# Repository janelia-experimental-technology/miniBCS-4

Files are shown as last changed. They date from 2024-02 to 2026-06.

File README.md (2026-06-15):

# miniBSC-4
 Configurable I/O PCB for Teensy 4.1 and Max11300
 
 https://doi.org/10.25378/janelia.29669162

 System Overview

The miniBCS is a compact, general-purpose Behavioral Control System (BCS). It provides a powerful platform to control real-time experiments. It is highly adaptable in terms of types of outputs and connectors. It is also designed to be easy to use, self-documenting, inexpensive, and easy to customize.

Hardware Development

The miniBCS is designed around the Teensy processor system. Currently, the Teensy 3.5 processor board is being used. This board utilizes a 32-bit ARM processor with 120Mhz operation, 512K Flash, and 192K RAM. The Arduino programming environment makes writing and downloading code easy. A MAX11300 integrated circuit provides 12-bit bipolar ADC/DAC and other configurable IO not available on the Teensy. The various input/outputs (IOs) are brought out to various connector options, including DB9, BNC, latch connectors, and RJ9. Connectors can face vertically or horizontally. A waveform generator is also built in. builders can add a small monochrome graphic LCD and three pushbuttons to provide a simple user interface. The system is designed so that only the required features and connectors need to be added to the base board, minimizing cost and assembly time. The enclosure can be made from laser-cut material, making it easy to configure the unit, house the electronics, make attachment points, and engrave connector labels.

Capabilities (some are mutually exclusive):

    Up to three RS232 serial ports
    Host USB serial port (also used for programming)
    CAN bus
    Ethernet
    Up to 10 12-bit DACs with +/-5V, 0-10V, or -10 to 10V ranges (MAX11300)
    Up to 10 12-bit ADCs with 0-2.5, +/-5V, 0-10V, or -10 to 0V ranges (MAX11300)
    Up to 10 IOs with programmable thresholds or output ranges (MAX11300)
    8 isolated solenoid drivers with 11-35 Volt power supply range
    Frequency Generator with a range of 1Hz to 10MHz, sine, triangle, square wave
    2 temperature sensors (MAX11300)
    SPI/I2C Expansion Bus
    Up to 8 IOs that connect directly to the processor that can be programmed for:
        Interrupts
        0-3.3V DAC
        0-3.3V ADC
        3.3V digital output
        5V tolerant digital input
        PWM or servo drive
        Various timer/counter needs

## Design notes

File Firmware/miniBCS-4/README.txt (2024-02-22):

# mimiBCS

An Arduino library to provide a high level interface for the miniBCS
This version handles boards from REV M and up

The miniBCS is an interface board for the Teensy 4.1 that provides BNC connections, Ethernet connection, I/O Expansion via a Maxim chip, 
drivers for RS232, solenoid drivers, encoder interface, and a waveform generator.

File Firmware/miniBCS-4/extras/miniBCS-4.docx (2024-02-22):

SPI LCD Panel Configuration and Setup

20170106 sws ID&F

The SPI-LCD (Serial Peripheral Interface Liquid Crystal Display) is used in lieu of the serial LCD panel in order to free up an additional serial port when needed to communicate with other peripheral devices. It is physically a direct replacement for the serial display, however, the Serial.print commands cannot be used with this display.

Firmware

The SPI-LCD library must be installed and the header file must be included at the top of the program:

#include <LCD2X16.h>

You need to create an instance of the LCD object outside of any functions:

LCD2x16 lcd;

The name ‘lcd’ is arbitrary. The examples assume ‘lcd’ is used as the object’s name.

In ‘setup()’ initialize the driver:

lcd.begin();

This will locate which SPI connector the board is connected to.

The following functions are available:

uint8_t csPin = lcd.getID();

Returns the number of the chip select pin for the display. This will depend on which SPI port the display is plugged into. There is generally no need to use this function.

lcd.setBacklight(uint8_t level);

Set the backlight level. ‘level’ should be between 0 and 8.

lcd.cls();

Clear the display.

lcd.write(char * string);

Write the character string ‘string’ to the display at the current cursor location.

lcd.setPosition(uint8_t row, uint8_t col);

Set the cursor to row ‘row’ and column ‘col’ – the top row is 0 and the left-most column is 0.

lcd.wrbyte(char c);

Send a single byte to the LCD. This can be used to send other display commands, such as setting special characters. See the NHD‐0216K3Z‐FL‐GBW‐V3 data sheet for details.

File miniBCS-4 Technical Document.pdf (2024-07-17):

# miniBCS-4

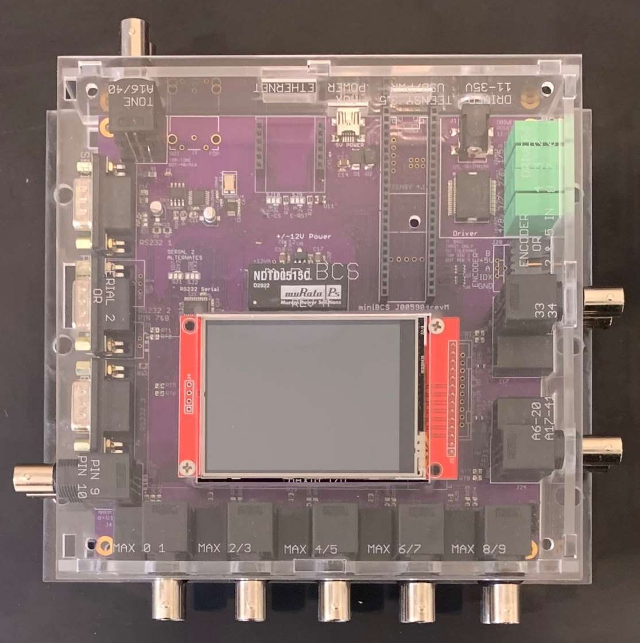
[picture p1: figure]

### Steve Sawtelle Engineer, ID&F

### Contents

System Overview | 2
Hardware Development | 2
Assembly | 4
Firmware | 6
miniBCS-4 Library Functions | 7
Enclosure | 8
Minimal Assembly of Bare PCB | 8

### System Overview

The miniBCS-4 is a compact, general purpose multi-function I/O system that makes it easy to access various peripherals found on the Teensy 4.1 and provides a powerful platform to control real time experiments. It is highly adaptable in terms of types of outputs and connectors and is designed to be easy to use, inexpensive, and easy to customize.

### Hardware Development

The miniBCS-4 is designed around the Teensy processor system. Currently, the Teensy 4.1 processor board is being used. The Arduino programming environment makes writing and downloading code easy. A MAX11300 integrated circuit is used to provide 12-bit bipolar ADC/DAC and other configurable I/O not available on the Teensy. The various input/outputs (IOs) are brought out to various connector options including DB9, BNC, latch connectors, and RJ9. A waveform generator is also built in. A color graphic LCD with touchscreen can be added to provide a simple user interface. Various sensors and other extensions can be easily added using I2C communications via a Qwiic connector and an SPI connector. The system is designed so that only the required features and connectors needed for a particular application are added to the base board, minimizing cost and assembly time. The enclosure can be made from laser cut acrylic, which makes it easy to configure the unit, house the electronics, make attachment points, and engrave connector labels.

Capabilities (some are mutually exclusive):

- Up to three RS232 serial ports
- Host USB serial port (also used for programming)
- Ethernet via WIZnet module
- Incremental Encoder (optional index pin) with 5V tolerant inputs
- Up to 10 12-bit DACs with +/-5V, 0-10V, or -10 to 10V ranges (MAX11300)
- Up to 10 12-bit ADCs with 0-2.5, +/-5V, 0-10V, or -10 to 0V ranges (MAX11300)
- Up to 10 I/Os with programmable thresholds or output ranges (MAX11300)
- 8 isolated solenoid drivers with 11-35 Volt power supply range
- Frequency Generator with range of 1Hz to 10MHz, sine, triangle, or square wave
- I/O Extension providing two direct processor I/Os and ten Maxim I/Os
- QWIIC I2C (as I2C number 2)
- SPI witn two chip selects
- Up to 9 I/Os that connect directly to the processor that can be programmed for: o Interrupts
o 0-3.3V ADC
o 3.3V digital output
o 3.3 digital input
o PWM or servo drive
o Various timer/counter needs

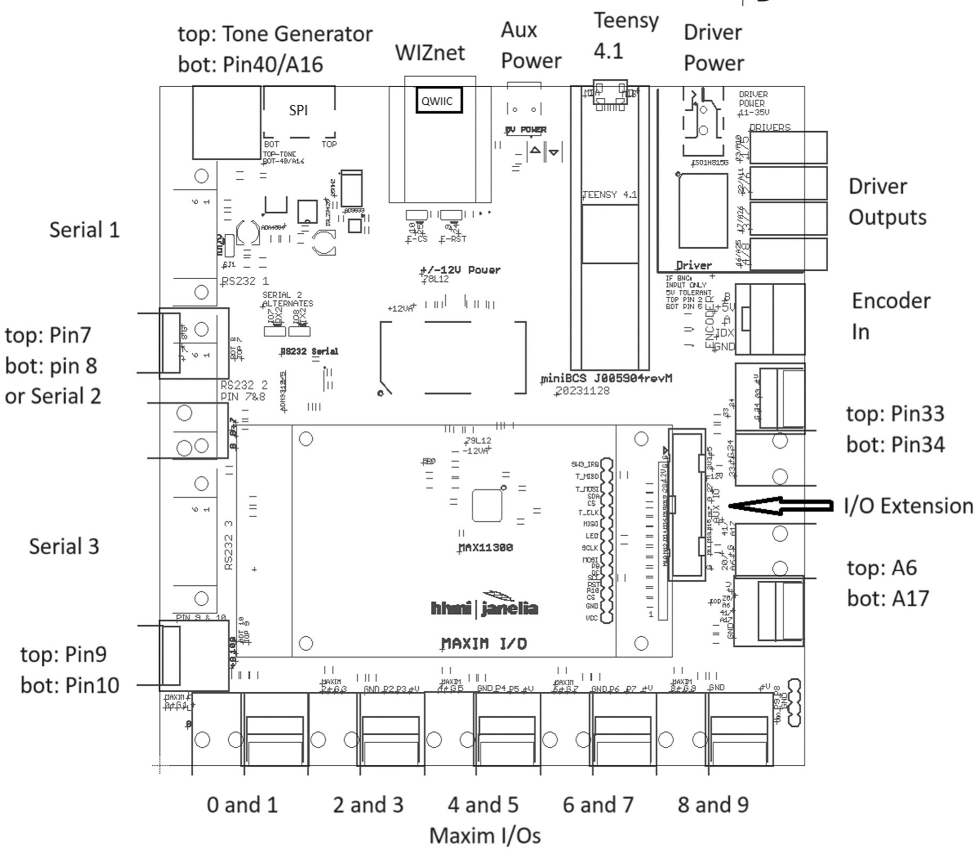
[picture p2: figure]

### Assembly

Due to the relative low cost and relative assembly difficulty of the surface mount parts on the board, it is advisable to have the basic board assembled by a small run assembly house. For 10 boards, this can be done for about $300 a board. For hand assembling partial boards, there is information at the end of the document. The real customization of the board is done by hardware jumpers, choice of connectors, and firmware. The jumpers and connectors can be easily soldered by hand by novices.

Note on Jumpers

Jumpers are included on the board to allow various configurations. There are two types of jumpers; I/O select, and tone select.

Pin selection jumpers have a connection to the default I/O. If the alternate function is needed, then the default connection between the pads needs to be cut and a short between the other function and the middle pad needs to be soldered in. These are used to select alternate CPU pins to be available at each connector to maximize I/O options. The following selections are available:

I/O | Jumper Name | Default | Option (cut and jumper)
RX2/IO7 | SJ1 | RS232 #2 Receive | Pin 7 (PWM, digital I/O)
TX2/IO8 | SJ2 | RS232 #2 Transmit | Pin 8 (PWM, digital I/O)
Eth-RST/IO9 | SJ9 | Pin 9 (PWM, digital I/O) | Alternate Ethernet Reset on Pin 9
Eth-CS/IO10 | SJ10 | Pin 10 (PWM, digital I/O) | Alternate Ethernet CS Pin 10

Tone Generator jumper (SJ1) allows the tone generator to bypass AC coupling and gain to provide a TTL square wave output. The default supports sine/triangle tones and AC couples the signal and provides variable gain. If a TTL square wave output is needed, then cut the jumper and solder the pads for square wave output. This bypasses the AC coupling and variable gain.

I2C (J11) provides a QWIIC compatible I2C interface using SDA2 and SCL2 from the Teesny 4.1. Be sure to specify ‘Wire2’ when setting the I2C clock and other initialization.

SPI (J3 or J26) provides an SPIO interface using either a ten-pin ribbon cable or a 7-pin 0.1 center connector. The ribbon cable is preferred as it provides grounds between the signals. Teensy pins 9 and 10 are brought out as chip selects, which would preclude their use on the J18/J19 connectors next to Serial Port 3.

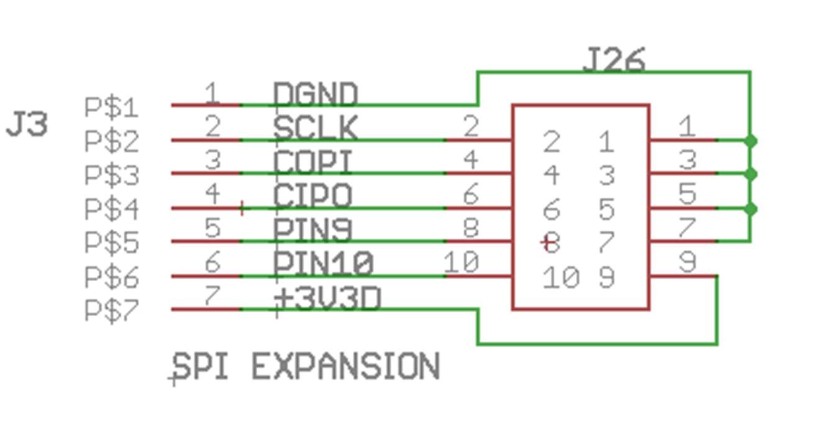
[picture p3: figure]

Auxiliary Input/Output (X2) Provides additional I/O through a 20-pin ribbon cable. Two unused Teensy I/O pins are brought out, along with the upper ten Maxim I/O pins, and power.

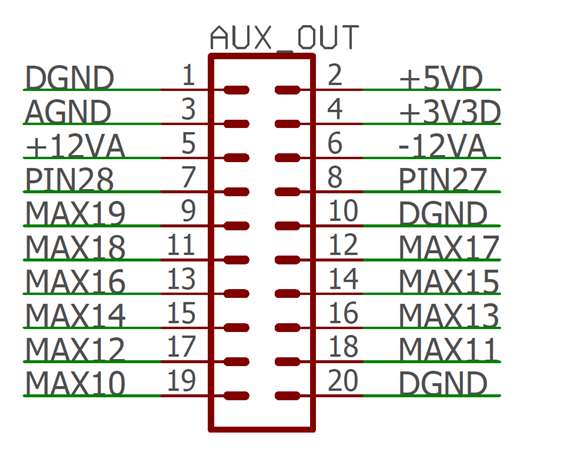
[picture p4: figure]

The available pins are:

### 1. Digital ground

2. +5 volts

### 3. Analog ground

4. +3.3 volts
5. +12 volts
6. -12 volts

### 7. Teensy pin 28 8. Teensy pin 27 9. Maxim I/O pin 19 10. Digital ground 11. Maxim I/O pin 18 12. Maxim I/O pin 17 13. Maxim I/O pin 16 14. Maxim I/O pin 15 15. Maxim I/O pin 14 16. Maxim I/O pin 13 17. Maxim I/O pin 12 18. Maxim I/O pin 11 19. Maxim I/O pin 10 20. Digital ground

### Firmware

The firmware is written under the Arduino environment. Download and install the Arduino software and add in the Teensy support. See the Arduino and PJRC websites for current implementations.

Add the miniBCS-4 library to your Arduino environment. This is available on the jET Experimental Technologies GitHub repository. This provides high level access to the drivers, tone generator, and encoder.

If the MAX11300 is used, add the MAX11300 library, also on the jET Experimental Technologies GitHub repository.

If the LCD is used, you will need to add the following Adafruit LCD libraries:

XPT2046_Touchscreen for Touchscreen functions.
ILI9341_t3.h for TFT Display functions.

The Adafruit website has good tutorial on how to use their functions.

Finally, if it is desired to have a command interface, then it may be worthwhile to look at the CmdArduino library, also found on the jET Experimental Technologies GitHub repository.

### miniBCS-4 Library Functions

These functions are available through the miniBCS-4 Arduino library.

void begin();
sets up hardware for I/O and interrupts
void driverOn(uint8_t ch);
turn on solenoid driver channel ‘ch’ void driverOff(uint8_t ch);
turn off solenoid driver ‘ch’
uint32_t getVersion(void);
return firmware version (year, month, day concatenated into a single integer – ex: 20190230 void setToneGain(uint8_t level);
set gain of tone output (0-255)
void toneReset(void);
reset frequency generator chip
int8_t setTone( float freq, uint16_t mode);
set tone to frequency ‘freq’ (1 to 20 MHz), and mode: TONE_SINE sine wave
TONE_TRIANGLE triangle wave TONE_SQUARE square wave
void toneOn(void);
enable tone output
void toneOff(void);
disable tone output
int32_t getPosition(void);
get encoder counts
void setPosition(uint32_t newpos);

set current value for encoder counts.

### Enclosure

An enclosure can be made from 1/8” laser cut acrylic. This allows the enclosure to be easily customized for the particular set of I/O connections mounted on the PCB. It also allows engraving unique labels for each connector.

A DXF file is provided that shows all the possible cutouts for various connector combinations.

### Minimal Assembly of Bare PCB

Only the parts needed for the application need to be assembled to the printed circuit board (PCB). At a minimum, the Teensy must be installed; everything else is optional. However, it is probably better to buy boards with all surface mount parts mounted and then add any required connectors and jumpers.

To decide what parts to install, first list the IOs needed for the application, then determine which IOs on the miniBCS-4 can fill the requirement. If only a few basic 0-3.3V digital and analog IOs are needed, the MAX11300 IC can be eliminated along with the DC-DC converter, power USB connector, and regulators. The parts that need to be added when the MAX11300 functions are needed are outlined on the PCB. If no solenoids, relays, or other power actuators are needed, the parts outlined in the solenoid driver area can be eliminated. If RS232 serial is not needed, then do not install the parts outlined in the RS232 area and change the jumper defaults for SJ1 and SJ2 by cutting the TX2 and RX2 track to the center pad and soldering from IO7 and IO8 to the center pad. This allows these pins to be used for additional IO.

Each IO will require a connector and in-line resistor (typically 100 ohms) or thermal cutout (PTC – such as the Murata PRG18BB series.

Minimal assembly:
Solder the headers for the Teensy

If any other ICs will be mounted, then D1 and D2 need to be installed.

If the MAX11300 functions are needed,
Add in the DC-DC converter, regulators, and filter caps, and resistors in that area. Solder in the components within that area

The connectors for each port pair can be:

### 1 Molex 0855135016 right angle RJ9 1 Amphenol 112705 right angle dual BNC

Both can coexist on the circuit board, but only one or the other should be connected to external circuits.

If the encoder is needed,
Solder in a TE 103635-4 right angle header
Mount U2. If the index pin is needed, then also add U8.

If the LCD is required
Solder a header in at LCD1. This can be a pluggable header or a flex cable to allow the LCD to be positioned elsewhere. A flex cable such as A9AAT-090xF can be used, where ‘x’ is the length in inches, 2, 3, 4, 5, 6, or 8.

If the solenoid driver is required
Solder the components in the Solenoid Parts area.

If RS232 serial ports are required
Solder in the parts in the RS232 Parts area
Solder in, for each port:

### 1 Norcomp 190-009-163R001 right angle DB9

If serial port 2 is not need, the pins can be brought out as additional I/O by cutting the serial jumpers SJ1 and SJ2 and solder jumper the alternate configuration pads.

If the tone generator is required
Solder in the parts in the TONE area. Also, if a TTL square wave is required, instead of the sine/triangle output cut the jumper at SJ3 and solder the alternative configuration.

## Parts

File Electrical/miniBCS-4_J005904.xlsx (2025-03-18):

J005904_miniBCSrevM- Three Serial Ports
Qty | Value | Device | Designators | Manufacturer | Man PN | Vendor | Vendor PN | $ea | $Total | Notes
2 | cap | CAP ALUM 22UF 20% 6.3V SMD | C9 C13 | Nichicon | UZP0J220MCL1GB | DK | 493-10070-1-ND | $0.50 | $1.00
1 | dc-dc | CONV DC/DC 3W 5VIN 15VOUT DIP24 | PS1 | Traco Power | TEN 3-0523N | DK | TEN3-0523N-ND | $16.40 | $16.40
1 | power in | CONN PWR JACK 2.5X5.5MM SOLDER | J1 | CUI | PJ-002BH-SMT-TR | DK | CP-002BHPJCT-ND | $1.29 | $1.29
2 | Schottky Diode | DIODE SCHOTTKY 15V 1A DO214AC | D1 D2 | Microsemi Corporation | LSM115JE3/TR13 | DK | LSM115JE3/TR13CT-ND | $1.17 | $2.34
24 | 0.1 | CAP CER 0.1UF 50V X7R 0603 | C1 C4 C6 C7 C8 C10 C14 C15 C19 C20 C21 C23 C24 C25 C26 C28 C29 C33 C34 C37 C38 C39 C40 C41 | Kemet | C0603C104K5RACTU | DK | 399-5089-1-ND | $0.03 | $0.72
1 | 0.1 | CAPS0805S | C16 |  |  | DK
1 | 1 | CAP CER 1UF 50V X7R 0805 | C11 | Kemet | C0805C105K5RACTU | DK | 399-7409-1-ND | $0.22 | $0.22
2 | 2K70 | RES SMD 2.7K OHM 1% 1/8W 0805 | R8 R13 | Vishay Dale | CRCW08052K70FKTA | DK | 541-2.70KCCT-ND | $0.05 | $0.10
6 | 4K99 | RES SMD 4.99K OHM 1% 1/8W 0805 | R2 R3 R6 R7 R26 R27 | Vishay Dale | CRCW08054K99FKEA | DK | 541-4.99KCCT-ND | $0.05 | $0.30
2 | 4R99 | RESISTOR_SM0805S | R14 R28 | Vishay Dale | CRCW08054R99FNEA | DK | 541-4.99CCT-ND | $0.06 | $0.12
2 | 10K0 | RES SMD 10K OHM 1% 1/8W 0805 | R16 R20 | Vishay Dale | CRCW080510K0FKTA | DK | 541-3016-1-ND | $0.14 | $0.28
9 | 10uF | CAP CER 10UF 25V X7R 1206 | C12 C17 C18 C27 C30 C31 C32 C35 C36 | Kemet | C1206C106M3RACTU | DK | 399-7443-1-ND | $0.51 | $4.59
1 | 78L12F | IC REG LDO 12V 0.1A SOT89-3 | U6 | ST Micro | L78L12ACUTR | DK | 497-1195-1-ND | $0.37 | $0.37
1 | 79L12 | IC REG LDO -12V 0.1A SOT89-3 | U9 | STMicro | L79L12ACUTR | DK | 497-7301-1-ND | $0.38 | $0.38
38 | 100 | THERMISTOR PTC 100 OHM SMD | RP1 - RP23, RT1 -RT8 | Murata | PRG18BB101MB1RB | DK | 490-2469-1-ND | $0.45 | $17.10
8 | 100 | RESISTOR_SM0805S | R1 R5 R17 R21 R22 R23 R24 R25 |  |  | DK
3 | 118 | RES SMD 118 OHM 1% 1/8W 0805 | R12 R15 R19 | Vishay Dale | CRCW0805118RFKEA | DK | 541-118CCT-ND | $0.05 | $0.15
1 | 1K25 | RES SMD 1K OHM 1% 1/8W 0805 | R4 | Vishay Dale | CRCW08051K00FKTA | DK | 541-1.00KAWCT-ND | $0.13 | $0.13 | ???
1 | AD9833 | IC WAVEFORM GEN PROG 10MSOP | U4 | Analog Devices | AD9833BRMZ-REEL7 | DK | AD9833BRMZ-REEL7CT-ND | $9.34 | $9.34
1 | ADA4084 | IC OPAMP GP 15.9MHZ RRO 8SOIC | U1 | Analog Devices | ADA4084-2ARZ-R7 | DK | ADA4084-2ARZ-R7CT-ND | $6.70 | $6.70
1 | ADM3312/5 | C TXRX RS-232 3:3 2.7V 24TSSOP | U7 | Analog Devices | ADM3312EARUZ-REEL7 | DK | ADM3312EARUZ-REEL7CT-ND | $3.50 | $3.50
1 | ISL23425 | ISL2342IC DGTL POT DUAL 10K 14TSSOP 5 | U3 | Intersil | ISL23425WFVZ-T7A | DK | ISL23425WFVZ-T7ACT-ND | $2.47 | $2.47
1 | ISO1H815G | IC SWITCH HISIDE 8CH DSO-36 | U5 | Infinion | ISO1H815G | DK | ISO1H815GCT-ND | $10.75 | $10.75
1 | MAX11300GCM | IC ADC 12BIT 48-TQFP | U10 | Maxim | MAX11300GCM+ | DK | MAX11300GCM+-ND | $14.74 | $14.74
1 | OSC-OE-CFPS-9 | 25MHz CMOS XO | X1 | AVX | KC5032A25.0000CM0E00 | DK | 1253-1043-1-ND | $1.46 | $1.46
2 | TEENSY_3_5_2 | CONN RCPT .100" 24POS SNGL GOLD | M1A, M1B | Samtec | SSQ-124-02-G-S | DK | SAM1187-24-ND | $4.64 | $9.28
1 | UX60-MB-5ST | CONN RECEPT MINI USB2.0 5POS | J2 | TE | 1734035-2 | DK | A31727CT-ND | $0.87 | $0.87
1 | CAT811 | IC SUPERVISOR PP ACT LO SOT143-4 | U11 | ON Semiconductor | CAT811TTBI-GT3 | DK | CAT811TTBI-GT3OSCT-ND | $0.43 | $0.43
 |  |  |  |  |  |  |  |  | $0.00
4 | Terminal Block | TERM BLOCK HDR 4POS 90DEG 2.5MM | J5 J6 J7 J8 | Phoenix | 1894804 | DK | 1894804-ND | $2.67 | $10.68
8 | plug for 1894804 | TERM BLOCK PLUG 2POS STR 2.5MM |  | Phoenix | 1881325 | DK | 277-1430-ND | $3.10 | $24.80
3 | DB9 | CONN DSUB PLUG 9POS SMD R/A SLDR | P1 P2 P3 | NorComp Inc. | 190-009-163R001 | DK | 190-09MA-ND | $2.85 | $8.55
 |  |  |  |  |  |  |  |  | $0.00
9 | Signal Alternate - BNC | BNC-DUAL | J4 J14 J19 J22 J27 J28 J29 J30 J31 | Amphenol | 112705 | DK | ACX2286-ND | $7.62 | $68.58
7 | Signal Alternate - RJ9 | CONN MOD JACK 4P4C R/A UNSHLD | J17 J21 J42 J43 J44 J45 J46 | Molex | 432024101 | DK | WM5439-ND | $1.54 | $10.78
 |  |  |  |  |  |  |  |  | $0.00
1 | Encoder | CONN HEADER R/A 4POS 2.54MM | J10 | TE Connectivity AMP Connectors | 5-103635-4 |  | A33864-ND | $1.39 | $1.39
 |  |  |  |  |  |  |  |  | $0.00
1 | Display | Color 320x240 TFT Touchscreen, ILI9341 Controller Chip | LCD1 | PJRC | DISPLAY_ILI9341_TOUCH | DK |  | $15.00 | $15.00
4 | LCD support | HEX STANDOFF #4-40 NYLON 1" |  |  | 4848 | DK | 36-4848-ND | $1.05 | $4.20
1 | LCD cable | FLEX CABLE - AFF14G/AF14/AFE14T | LCD1 | TE Connectivity AMP Connectors | A9BAG-1402F |  | A9BAG-1402F-ND | $4.89 | $4.89
1 | SPI connector | CONN HEADER R/A 10POS 2.54MM | J26 | 3M | 30310-5002HB |  | 3M15452-ND | $1.01 | $1.01
1 | qwiic Connector | Surface Mount, Right Angle 4 pos 1.00mm | J11 | JST Sales America Inc. | SM04B-SRSS-TB |  | 455-SM04B-SRSS-TBCT-ND | $0.60 | $0.60
2 | 2ch buffers | IC BUF NON-INVERT 5.5V SOT23-6 | U2 U8 | TI | SN74LVC2G17DBVR |  | 296-SN74LVC2G17DBVRCT-ND | $0.40 | $0.80
1 | Networking Modules W5500 + MAG Jack |  |  | WIZnet | WIZ850IO |  |  | $21.98 | $21.98
2 | Headers & Wire Housings Tiger Buy Socket Strip with Square Tails, 0.100 Pitch |  |  | Samtec | SSQ-106-01-G-S |  |  | $1.35 | $2.70
 |  |  |  |  |  |  |  |  | $280.99

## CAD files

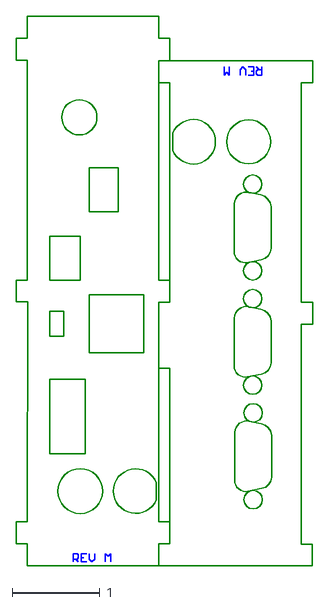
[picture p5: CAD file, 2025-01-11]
Mechanical/untitled.dxf
3.37 x 6.25

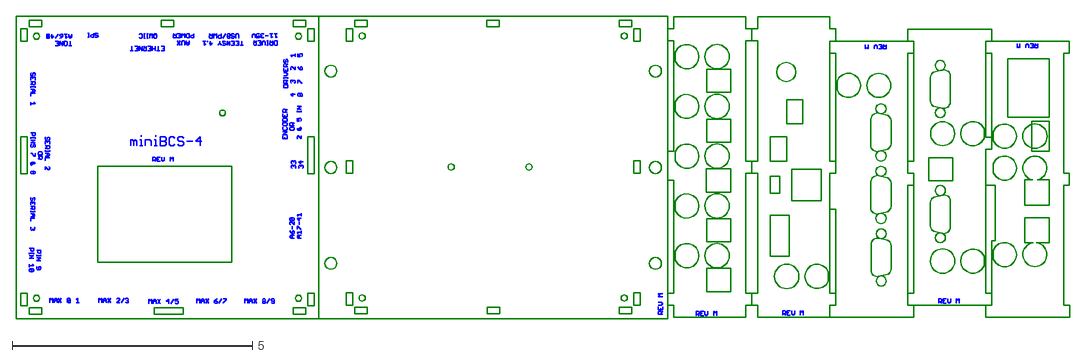
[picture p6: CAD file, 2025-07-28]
Mechanical/J005904_miniBCS-4.dxf
21.9 x 6.30

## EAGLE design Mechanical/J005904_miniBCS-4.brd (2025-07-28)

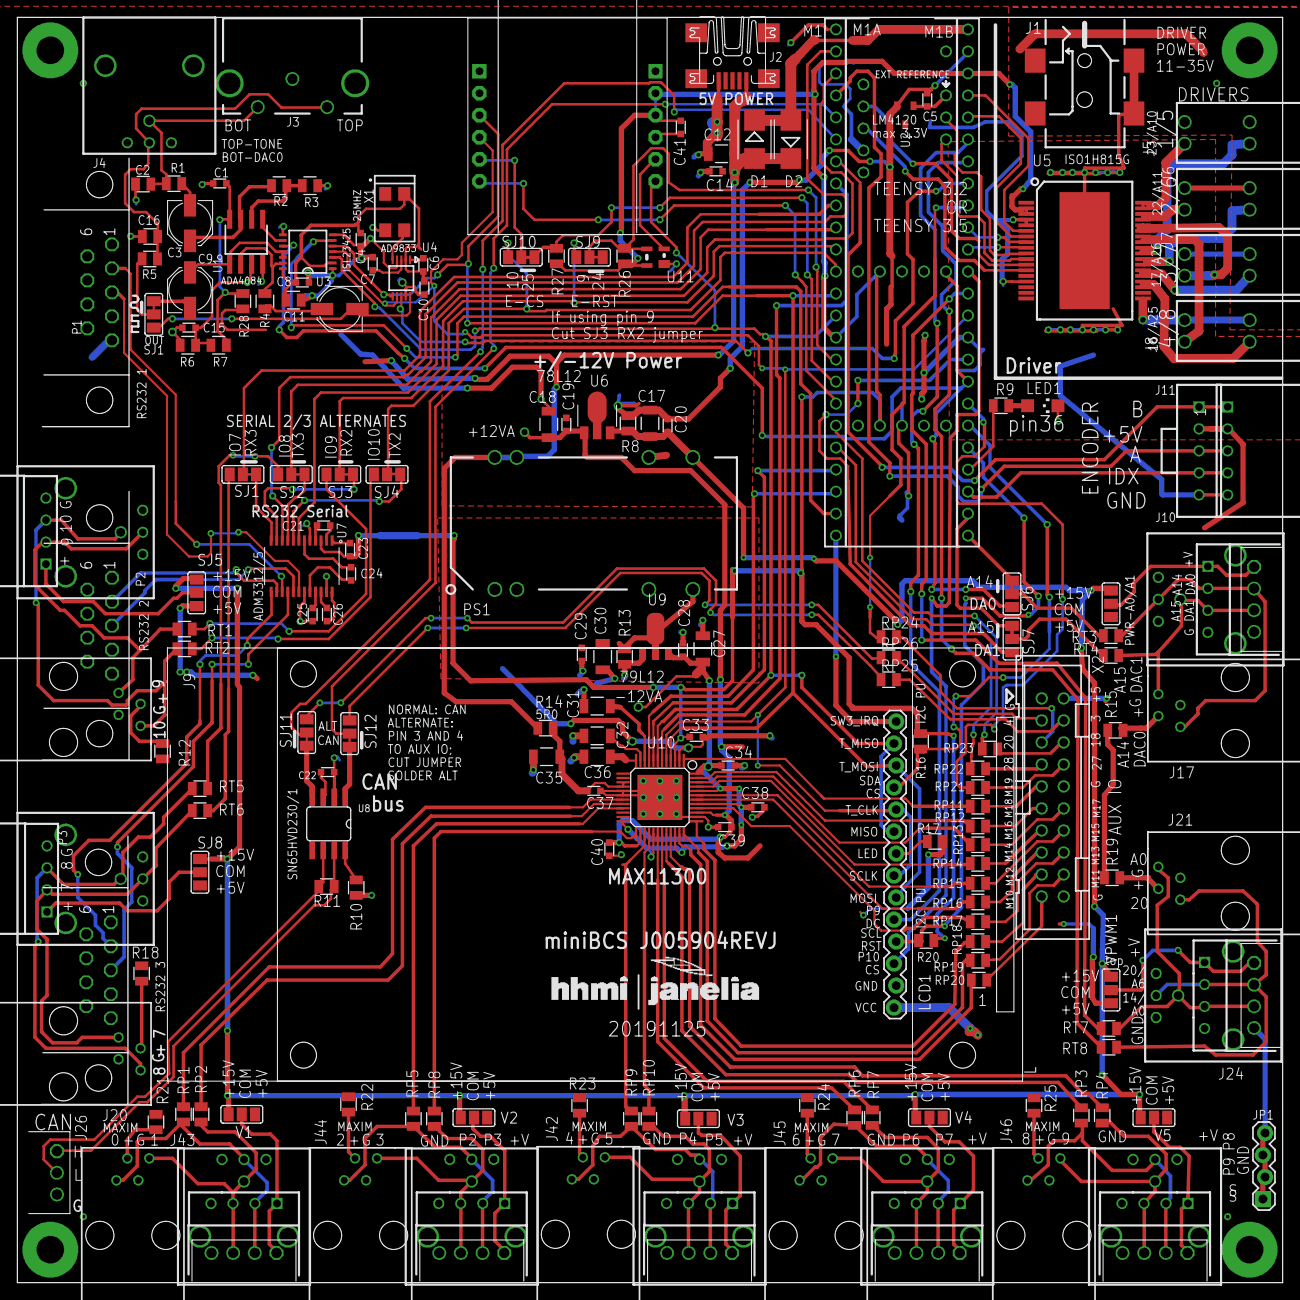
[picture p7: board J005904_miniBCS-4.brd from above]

Board: 2 copper layers, 146.1 x 146.1 mm, 199 parts (1 on the bottom side), 185 nets.

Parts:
C1, C4, C6, C7, C8, C10, C14, C15, C19, C20, C21, C23, C24, C25, C26, C28, C29, C33, C34, C37, C38, C39, C40: 0.1; 0603S
C2, C16: 0.1; 0805S
C3, C9, C13: PANASONIC_C
C5, C22, C41: .1uF; 0603S
C11: 1; 0805S
C12, C17, C18, C27, C30, C31, C32, C36: 10; 1206S
C35: 10uF; 1206S
D1, D2: SMB
FID1, FID2, FID3, FID4: FIDUCIAL_VIA
IC1: WIZ820IO
J1: PJ-002
J2: UX60-MB-5ST
J3: RCA_DUAL; RCJ-22XX
J4, J13, J19, J22, J27, J28, J29, J30, J31: DUAL-BNC
J5, J6, J7, J8: 1894804
J9, J17, J20, J21, J42, J43, J44, J45, J46: 0432024101
J10: AMPMODU-5
J11: 103635-4
J12, J15, J18, J23, J32, J33, J34, J35, J36: AMPMODU-4-RA
J14: A0/A1; DUAL-BNC
J16, J24, J37, J38, J39, J40, J41: PHOENIX_1881464
J26: PHOENIX_1881451
JMP100: JUMPER
JP1: 1X04_LOCK
L: ILI9341TFT_FP; ILI9341TFT_HOLES
LCD1: TFT_LCDTFT_NOHOLES; TFT_LCD_NOHOLES
LED1: CHIPLED_1206
M1: TEENSY_3_5_2; TEENSY_3.X
OUT: SJ1; SJ_2
P1, P2, P3: 182-009-MALE
PS1: NDTD
PWR-A0/A1: SJ_2
R1, R5, R9, R17, R21, R22, R23, R24, R25: 100; 0805S
R2, R6, R7: 4K99; 0805S
R3, R16, R20, R26, R27: 10K0; 0805S
R4: 1250; 0805S
R8, R13: 2K70; 0805S
R10, R11, R12, R15, R18, R19: 118; 0805S
R14, R28: 4R99; 0805S
RP1, RP2, RP3, RP4, RP5, RP6, RP7, RP8, RP9, RP10, RP11, RP12, RP13, RP14, RP15, RP16, RP17, RP18, RP19, RP20, RP21, RP22, RP23, RP24, RP25, RP26: 100; 0805S
RT1, RT2, RT3, RT4, RT5, RT6, RT7, RT8: 100; 0805S
SJ1, SJ2, SJ3, SJ4, SJ5, SJ6, SJ7, SJ8, SJ9, SJ10, SJ11, SJ12: SJ_2
U1: ADA4084; SO8
U2: LM4120; DBZ_R-PDSO-G3
U3: ISL23425; TSSOP14
U4: AD9833; MSOP10
U5: ISO1H815G; PG-DSO-36
U6: 78L12; SOT89
U7: ADM3312/5; TSSOP-24
U8: SN65HVD230/1; SO8
U9: 79L12; SOT89
U10: MAX11300GCM; TQFP48
U11: CAT811; SOT-143
U$1: JFRC-LOGOLOGO_2014_DOC; LOGO_JANELIA_2014_DOC
V1, V2, V3, V4, V5: SJ_2
VPWM1: SJ_2
X1: OSC-OE-CFPS-9; 5.2X3.4-4-PAD
X2: 2520-; PAK100/2500-20

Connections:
0.1: C22.1, U8.3
!CS_DDS: M1.19/A5, U4.8
!CS_POT: M1.31/A12, U3.6
!MAXCNVT: M1.30, U10.9
!MAXINT: M1.29, U10.8
!MAX_CS: M1.6, U10.6
!TFT_CS: LCD1.3, M1.15/A1
+2V5A: C15.1, R6.2, R7.1, U1.3
+3V3D: C23.2, C33.1, C41.2, IC1.J2.2, IC1.J2.3, M1.3.3V, M1.3.3V3, M1.3.3V4, M1.3.3V_32, R16.1, R20.1, R26.1, R27.1, U5.2, U5.3, U7.3, U10.3, U11.4
+5VA: C35.1, C37.1, R14.1, U10.15, U10.16
+5VADDS: C1.1, R7.2, R28.1, U1.8
+5VD: C4.1, C6.2, C8.2, C10.1, C11.1, C12.1, C14.1, D1.A, D2.C, J2.1, J10.2, J11.2, LCD1.1, PS1.22, PS1.23, PWR-A0/A1.1, R12.2, R14.2, R15.1, R17.1, R18.2, R19.1, R21.2, R22.2, R23.2, R24.2, R25.2, R28.2, SJ5.1, SJ8.1, U3.2, U3.14, U4.2, V1.1, V2.1, V3.1, V4.1, V5.1, VPWM1.1, X1.4, X2.2
+12VA: C18.1, C19.1, C39.1, C40.1, U6.1, U10.26, U10.39
+15V: C17.1, C20.1, PS1.14, PWR-A0/A1.3, R8.1, SJ5.3, SJ8.3, U6.3, V1.3, V2.3, V3.3, V4.3, V5.3, VPWM1.3
-12VA: C27.2, C28.2, C34.1, C38.1, U9.3, U10.24, U10.29, U10.34, U10.41, U10.44, U10.48
-15V: C29.2, C30.2, PS1.11, R13.2, U9.2, U9.2@1
A0: M1.14/A0, RT7.2
A14: M1.33/A14, RT3.2, SJ6.2, SJ6.3
A15: M1.34/A15, RT4.2, SJ7.2, SJ7.3
AGND: C1.2, C2.2, C5.2, C10.2, C15.2, C16.2, C17.2, C18.2, C19.2, C20.2, C27.1, C28.1, C29.1, C30.1, C31.2, C32.2, C34.2, C35.2, C36.2, C37.2, C38.2, C39.2, C40.2, J3.1, J4.P$3, J4.P$4, J27.P$3, J27.P$4, J28.P$3, J28.P$4, J29.P$3, J29.P$4, J30.P$3, J30.P$4, J31.P$3, J31.P$4, J32.4, J33.4, J34.4, J35.4, J36.4, J37.4, J38.4, J39.4, J40.4, J41.4, J42.3, J43.3, J44.3, J45.3, J46.3, JMP100.1, M1.AGND, PS1.9, PS1.16, R3.2, R6.1, R8.2, R13.1, U1.4, U2.2, U3.8, U4.9, U6.2, U6.2@1, U9.1, U10.17, U10.18, U10.38, U10.P$1
AREF: C5.1, M1.AREF, U2.1
CANH: J26.1, R11.1, U8.7
CANL: J26.2, R11.2, U8.6
CANRX: M1.4, SJ11.2, SJ11.3, U8.4
CANTX: M1.3, SJ12.2, SJ12.3, U8.1
DAC0: M1.A14/DAC_32, M1.A21, SJ6.1, U3.10
DAC0_OUT: C2.1, J3.2, J4.P$1, R1.2
DAC1: M1.A22, SJ7.1
DAC_REF: C36.1, U10.12
DDS: C13.-, OUT.1, U4.10
DDS_OUT: C16.1, J3.3, J4.P$2, R5.2
DGND: C4.2, C7.2, C8.1, C11.2, C12.2, C14.2, C22.2, C25.2, C33.2, C41.1, IC1.J1.1, IC1.J1.2, IC1.J2.1, IC1.J2.4, J2.5, J9.3, J10.5, J11.5, J12.4, J13.P$3, J13.P$4, J14.P$3, J14.P$4, J15.4, J16.4, J17.3, J18.4, J19.P$3, J19.P$4, J20.3, J21.3, J22.P$3, J22.P$4, J23.4, J24.4, J26.3, JMP100.2, JP1.1, JP1.2, JP1.3, JP1.4, LCD1.2, LED1.C, M1.GND, M1.GND1, M1.GND3, M1.GND4, M1.GND6, M1.GND_32, P1.5, P2.5, P3.5, PS1.2, PS1.3, R10.1, U3.1, U3.7, U4.4, U5.4, U5.5, U5.15, U7.5, U7.19, U7.23, U8.2, U10.2, U11.1, X1.2, X2.1, X2.10, X2.20
EA: J28.P$2, J33.2, J38.2, J43.1, RP1.1
EA1: J29.P$2, J34.2, J39.2, J44.1, RP5.1
EA2: J30.P$2, J35.2, J40.2, J42.1, RP9.1
EA3: J31.P$2, J36.2, J41.2, J45.1, RP6.1
EA4: J27.P$2, J32.2, J37.2, J46.1, RP3.1
EA5: J14.P$2, J15.2, J16.2, J17.1, RT3.1
EA6: J21.1, J22.P$2, J23.2, J24.2, RT8.1
EA7: J18.2, J19.P$2, J20.1, RT6.1
EA8: J9.1, J12.2, J13.P$2, RT1.1
EB: J28.P$1, J33.3, J38.3, J43.4, RP2.1
EB1: J29.P$1, J34.3, J39.3, J44.4, RP8.1
EB2: J30.P$1, J35.3, J40.3, J42.4, RP10.1
EB3: J31.P$1, J36.3, J41.3, J45.4, RP7.1
EB4: J27.P$1, J32.3, J37.3, J46.4, RP4.1
EB5: J14.P$1, J15.3, J16.3, J17.4, RT4.1
EB6: J21.4, J22.P$1, J23.3, J24.3, RT7.1
EB7: J18.3, J19.P$1, J20.4, RT5.1
EB8: J9.4, J12.3, J13.P$1, RT2.1
EN_A: J10.3, J11.3, M1.2
EN_B: J10.1, J11.1, M1.5
ETH_CS: IC1.J1.5, M1.25, R27.2, SJ10.2, SJ10.3
ETH_INT: IC1.J1.6, M1.26
ETH_RST: M1.24, R26.2, SJ9.2, SJ9.3, U11.3
EXT_REF: C32.1, U10.11
GNDBB: J1.2, J5.2, J5.4, J6.2, J6.4, J7.2, J7.4, J8.2, J8.4, U5.19
IDX: J10.4, J11.4, M1.35/A16
INT_REF: C31.1, U10.10
MISO: IC1.J2.6, LCD1.9, LCD1.13, M1.12, U3.3, U10.7
MOSI: IC1.J1.3, LCD1.6, LCD1.12, M1.11, U3.5, U4.6, U10.4
unnamed: J20.2, R18.1
unnamed: J7.1, U5.23, U5.24
unnamed: J9.2, R12.1
unnamed: J21.2, R19.2
unnamed: U1.5, U3.9
unnamed: M1.36/A17, R9.2
unnamed: R2.1, R3.1, U1.6
unnamed: J17.2, R15.2
unnamed: P2.2, U7.14
unnamed: J5.1, U5.27, U5.28
unnamed: P2.3, U7.17
unnamed: C23.1, U7.1
unnamed: U4.5, X1.3
unnamed: J6.1, U5.25, U5.26
unnamed: C25.1, U7.21
unnamed: P1.3, U7.18
unnamed: J8.3, U5.29, U5.30
unnamed: J8.1, U5.21, U5.22
unnamed: LED1.A, R9.1
unnamed: C7.1, U4.3
unnamed: C26.2, U7.24
unnamed: C6.1, U4.1
unnamed: C26.1, U7.22
unnamed: J43.2, R21.1
unnamed: C21.1, U7.4
unnamed: C21.2, U7.2
unnamed: C24.1, U7.20
unnamed: P1.2, U7.15
unnamed: J42.2, R23.1
unnamed: J5.3, U5.35, U5.36
unnamed: C24.2, U7.6
unnamed: J6.3, U5.33, U5.34
unnamed: J46.2, R25.1
unnamed: C13.+, R4.1
unnamed: J45.2, R24.1
unnamed: R4.2, U1.2, U3.13
unnamed: C3.+, R2.2, U1.7
unnamed: C9.+, U1.1, U3.11, U3.12
unnamed: R10.2, U8.8
unnamed: J7.3, U5.31, U5.32
unnamed: J44.2, R22.1
unnamed: RP15.2, X2.14
unnamed: P3.3, U7.16
unnamed: RP14.2, X2.13
unnamed: IC1.J2.5, U11.2
unnamed: RP20.2, X2.19
unnamed: RP19.2, X2.18
unnamed: RP18.2, X2.17
unnamed: RP17.2, X2.16
unnamed: RP16.2, X2.15
unnamed: RP13.2, X2.12
unnamed: RP12.2, X2.11
unnamed: RP11.2, X2.9
unnamed: RP21.2, X2.8
unnamed: RP22.2, X2.7
unnamed: RP23.2, X2.6
unnamed: RP24.2, X2.5
unnamed: RP25.2, X2.4
unnamed: RP26.2, X2.3
P0: RP1.2, U10.19
P1: RP2.2, U10.20
P2: RP5.2, U10.21
P3: RP8.2, U10.25
P4: RP9.2, U10.27
P5: RP10.2, U10.28
P6: RP6.2, U10.30
P7: RP7.2, U10.31
P8: RP3.2, U10.32
P9: RP4.2, U10.33
P10: RP20.1, U10.35
P11: RP19.1, U10.36
P12: RP18.1, U10.37
P13: RP17.1, U10.40
P14: RP16.1, U10.42
P15: RP15.1, U10.43
P16: RP14.1, U10.45
P17: RP13.1, U10.46
P18: RP12.1, U10.47
P19: RP11.1, U10.1
PIN7: RT6.2, SJ1.3
PIN8: RT5.2, SJ2.3
PIN9: RT1.2, SJ3.3
PIN10: RT2.2, SJ4.3
PIN_3: RP26.1, SJ12.1
PIN_4: RP25.1, SJ11.1
PIN_18: M1.18/A4, RP24.1
PIN_20: M1.20/A6, RT8.2
PIN_27: M1.27, RP23.1
PIN_28: M1.28, RP22.1
PIN_39: M1.39/A20, RP21.1
PWR7_8: J18.1, SJ8.2
PWR9_10: J12.1, SJ5.2
PWRA0_A1: J15.1, J16.1, PWR-A0/A1.2
PWRPWM1_2: J23.1, J24.1, VPWM1.2
PWR_P0-1: J33.1, J38.1, V1.2
PWR_P2-3: J34.1, J39.1, V2.2
PWR_P4-5: J35.1, J40.1, V3.2
PWR_P6-7: J36.1, J41.1, V4.2
PWR_P8-9: J32.1, J37.1, V5.2
RX1: M1.0, U7.10
RX2: M1.9, SJ3.1, SJ3.2, SJ9.1, U7.11
RX3: M1.7, SJ1.1, SJ1.2, U7.12
RX3_232: P3.2, U7.13
SCL: LCD1.4, M1.37/A18, R20.2
SCLK: IC1.J1.4, LCD1.7, LCD1.10, M1.13, U3.4, U4.7, U10.5
SDA: LCD1.11, M1.38/A19, R16.2
SJ1: C9.-, OUT.2, OUT.3, R5.1
SOL1: M1.23/A9, U5.6
SOL2: M1.22/A8, U5.7
SOL3: M1.17/A3, U5.8
SOL4: M1.16/A2, U5.9
SOL5: M1.A10, U5.10
SOL6: M1.A11, U5.11
SOL7: M1.A26, U5.12
SOL8: M1.A25, U5.13
SW1: LCD1.14, M1.32/A13
TFT_DC: LCD1.5, M1.21/A7
TFT_LED: LCD1.8, R17.2
TX1: M1.1, U7.7
TX2: M1.10, SJ4.1, SJ4.2, SJ10.1, U7.8
TX3: M1.8, SJ2.1, SJ2.2, U7.9
VBB: J1.1A, J1.1B, U5.P$1
VIN: D1.C, D2.A, M1.VIN
VOUTB_1: C3.-, R1.1

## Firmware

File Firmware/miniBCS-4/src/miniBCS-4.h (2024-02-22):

// ----------------------------------------------------------------------------
// miniBCS
// 
// functions needed for the miniBCS
//  set up solenoid pins, pushbutton pins 
//
// Author: Steve Sawtelle
// HHMI Janelia ID&F
// ----------------------------------------------------------------------------

// ---- VERSIONS  ----
#define  miniBCS_VERSION ((uint32_t) 20231129) 

// 0231129 sws
// - remove depracted Button code
// - changes for 'M' board with Teensy 4.1

// 20230518 sws
// - SOL7PIN was set to pin 4 and SOL8 to pin 3, but hardware is opposite, fix in FW

// 20221205 sws
// - solenoid pins 5-8 on Teesny 3.5 cannot be used as digital out
//   so set them the same as the T4.1. This will interfere with CAN 

// 20220822 sws
//  - add GPO pins 16 to 19 NOTE: Should also extend GPI and analog as well

// 20220613 sws 
// - alt pins for Teensy 4.1 - here and .cpp

// 20190322 sws
// - add CS setups for TFT and touchscreen so BCS can init properly

// 20190315 sws
// - mods for REV G boards
//  	- LCDCS now SPAREpin
//		- pin 15 now TFT CS
//		- SCL now TFT reset
//		- SDA now touchscreen CS
// 		- SW1 is TS int
// 		- 21 is TFT data/command

// 20170906 sws
// - add MAX code
// - workaround for problem with SPI settings
// 20170824 sws
// - change PB to use HW debounce
// - add encoder

// 20170817
// - started


#ifndef miniBCS_H
#define miniBCS_H

#include <SPI.h>

//volatile uint8_t _pushButtons = 0;

class miniBCS
{
 public:
 
//=======================================
// === P I N    D E F I N I T I O N S ===
// ======================================

#define RX1pin    0   // Serial 1 RX 
#define TX1pin    1   // Serial 1 TX
#define ENCApin   2   // encoder 'A' pin
#define SOL7pin   3 // Solenoid 7 pin
#define SOL8pin   4 // Solenoid 8 pin
#define ENCBpin   5   // encoder 'B' pin
#define MAXCSpin  6   // Chip Select for MAX112300
#ifdef ARDUINO_TEENSY41
#define RX2pin    7   // 
#else
#define RX3pin    7   // Serial 3 RX or 
#endif
#define PIN7      7   //   IO pin, with PWM
#ifdef ARDUINO_TEENSY41
#define TX2pin    8   // 
#else
#define TX3pin    8   // Serial 3 TX or
#endif
#define PIN8      8   //   IO pin with PWM
#define PIN9      9   //   IO pin with PWM
#ifndef ARDUINO_TEENSY41
#define RX2pin    9   // Serial 2 RX or
#define TX2pin    10  // Serial 3 TX or
#endif
#define PIN10     10  //   IO pin with PWM
#define ETHCSpin  10  // or alternate ethernet CS
#define MOSIpin   11  // SPI MOSI
#define MISOpin   12  // SPI MISO
#define SCLKpin   13  // SPI Clock
#ifdef ARDUINO_TEENSY41
#define TX3pin    14   // 
#endif
#define A0pin     14  // Analog in A0
#ifdef ARDUINO_TEENSY41
#define RX3pin    15
#else
#define TFTCSpin  15  // TFT chip select 
#endif
#define SOL4pin   16  // Solenoid 4 pin
#define SOL3pin   17  // Solenoid 3 pin
#define SOL5pin   18  // Solenoid 5 pin
#define DDSCSpin  19  // Chip Select for DDS
#define A6pin     20  // Analog in A6 
#define PIN20     20  //	or IO 20
#define TFTDCpin  21  // TFT Display command/data	or IO 21
#define SOL2pin   22  // Solenoid 2 pin
#define SOL1pin   23  // Solenoid 1 pin
#define ETH_RSTpin  24  // reserved for Ethernet
#define ETH_CS    25  // reserved for Ethernet
#define ETH26pin  26  // reserved for Ethernet
#define EXP8pin   27  // to Expansion Connection 8
#define EXP7pin   28  // to Expansion Connection 7
#define MAXINTpin 29  // interrupt in from MAX11300
#define MAXCVTpin 30  // ADC Convert signal to MAX11300
#define POTCSpin  31  // Chip Select for digital pot
#define TSINTpin  32  // touch screen interrupt	
#define PIN33     33  // I/O pin 33 w PWM
#define PIN34     34  // I/O pin 34 
#define IDXpin    35  // Encoder Index in
#ifdef ARDUINO_TEENSY41
#define TFTCSpin  36   // 
#else
#define LED1pin   36  // LED pin, Auxiliary I/O, analog, PWM for auxiliary connector - depracted 'M' rev and later 
#endif
#define TFTRSTpin 37  // TFT RESET  analog, PWM , SCL
#define TSCSpin   38  // Touchscreen CS, SDA
#define SOL6pin   39 // Solenoid 6 pin
#ifndef ARDUINO_TEENSY41
#define DAC0pin   A21 // DAC0 out pin (must be jumpered)
#define DAC1pin   A22 // DAC1 out pin (must be jumpered)
#endif


// DDS output waveform types
#define TONE_SINE     0x0000
#define TONE_TRIANGLE 0x0002  
#define TONE_SQUARE   0x0028   
#define TONE_DIVIDE   0x0020  


// MAX11300 defines
#define DAC_DATA_PORT_00 0x60
#define GPO_DATA_15_TO_0 0x0d
#define GPO_DATA_19_TO_16 0x0e
#define ADC_DATA_PORT_00 0x40
#define GPI_DATA_15_TO_0 0x0b
#define INT_TEMP		 0x08
#define EXT_TEMP1		 0x09
#define EXT_TEMP2		 0x0a
#define MAX_INT				0x01
#define MAX_ADCFLAG_MASK	0x0001
#define MAX_ADCST_L			0x02	
#define MAX_ADCST_H			0x03
#define MAX_ADCDM_MASK		0x0004
#define MAX_ADCDR_MASK		0x0002	
#define MAX_ADCFLAG_MASK	0x0001


  miniBCS(void);
  
  void begin();
  void driverOn(uint8_t ch);					// turn on driver channel 'ch'
  void driverOff(uint8_t ch);					// turn off driver channel 'ch'
  int8_t getDriver(uint8_t ch);					// get status of channel 'ch' (false = off)
  uint32_t getVersion(void);					// get library version (year,month,date )
  void setToneGain(uint8_t level);				// set tone output level (0-255)
  void toneReset(void);							// reset tone generator chip
  int8_t setTone( float freq, uint16_t mode);	// set tone frequency and waveform type	
  void toneOn(void);							// enable tone (that has already been set up)
  void toneOff(void);							// disable tone without changing parameters	
  int32_t getPosition(void);					// get encoder position (cumulative counts)
  void  setPosition(int32_t newpos);			// set encoder position to a value
  uint16_t getToneMode(void); 					// read waveform type set on tone generator
 
   
 private:
 
  const static uint16_t DDS_CONTROL =  0x2000;   // 0010 0000 0000 0000
  const static uint32_t DDS_MCLK = 25000000;  
  const static uint32_t DDS_2_28 = 268435456; 
 
  // Private Constants
  volatile uint32_t encoderCount;
  volatile float distancePerTick;
  volatile float speedPerTickPerSec;
  volatile uint32_t zeroMillis;
  
  uint16_t freqMode; 
  uint32_t ifreq;
  uint16_t fwordl;
  uint16_t  fwordh;
  uint8_t SOUND_ON_OFF = 1; //each channel is off to begin with, correlating to a value of 1 for D6
  const uint8_t driverPin[9] = {0, SOL1pin, SOL2pin, SOL3pin, SOL4pin, SOL5pin, SOL6pin, SOL7pin, SOL8pin};
  int8_t driverOnOff = 0x00;

};  // endclass miniBCS


#endif // miniBCS

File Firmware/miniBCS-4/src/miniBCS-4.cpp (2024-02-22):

// ----------------------------------------------------------------------------
// miniBCS
// 
// functions needed for the miniBCS
//
// Author: Steve Sawtelle
// HHMI Janelia ID&F
// ----------------------------------------------------------------------------
#if defined(ARDUINO) && ARDUINO >= 100
#include "Arduino.h"
#else
#include "WProgram.h"
#endif

#include "miniBCS-4.h"


//---------- constructor ----------------------------------------------------

// volatile uint8_t _pushButtons = 0;
volatile int32_t _position = 0;

volatile uint32_t	_analogStatus = 0;
volatile bool		_analogFlag;

miniBCS::miniBCS(void)
{
;
}
//------------------ private -----------------------------------------------


 SPISettings POT_SPI(2000000, MSBFIRST, SPI_MODE0);   // clk idle low, rising egde
 SPISettings DDS_SPI(5000000, MSBFIRST, SPI_MODE2);   // clk idle high, falling edge
// SPISettings MAX_SPI(5000000, MSBFIRST, SPI_MODE0);   // 


void EncoderA_interrupt_handler()
{
  // figure out the direction  
  if (digitalRead(ENCApin) == digitalRead(ENCBpin))
    _position--;
  else
    _position++;
}


// ---------------- public -----------------------------------------------------------

 void miniBCS::begin(void)
{
	// init all SPI chip selects 
	
    pinMode(MAXCSpin, OUTPUT);
    digitalWrite(MAXCSpin, HIGH);
	   

	pinMode( DDSCSpin, OUTPUT);
	digitalWrite( DDSCSpin, HIGH);	
	

	pinMode( POTCSpin, OUTPUT);	
	digitalWrite( POTCSpin, HIGH);	
	
	
	SPI.begin();


	pinMode(SOL1pin, OUTPUT);
	pinMode(SOL2pin, OUTPUT);	
	pinMode(SOL3pin, OUTPUT);
	pinMode(SOL4pin, OUTPUT);
	pinMode(SOL5pin, OUTPUT);
	pinMode(SOL6pin, OUTPUT);	
	pinMode(SOL7pin, OUTPUT);
	pinMode(SOL8pin, OUTPUT);	

	digitalWrite(SOL1pin, LOW);
	digitalWrite(SOL2pin, LOW);
	digitalWrite(SOL3pin, LOW);
	digitalWrite(SOL4pin, LOW);
	digitalWrite(SOL5pin, LOW);
	digitalWrite(SOL6pin, LOW);
	digitalWrite(SOL7pin, LOW);
	digitalWrite(SOL8pin, LOW);	
		
	pinMode(ENCApin, INPUT_PULLUP);  // encoder inputs
    pinMode(ENCBpin, INPUT_PULLUP);
    pinMode(IDXpin, INPUT_PULLUP);

	
	attachInterrupt( ENCApin, EncoderA_interrupt_handler, RISING);

	SPI.beginTransaction(DDS_SPI);
	digitalWrite( DDSCSpin, LOW);		
	SPI.transfer16(0x2100);     // write control reg
	digitalWrite( DDSCSpin, HIGH);	
	SPI.endTransaction();
  
} 


uint32_t miniBCS::getVersion(void)
{
    return(miniBCS_VERSION);	
}

void miniBCS::driverOn(uint8_t ch)
{
	 
	if( (ch >= 1) && (ch <= 8) )
    {		
		digitalWrite( driverPin[ch], HIGH);
		driverOnOff |= (1 << (ch-1));
	}	
	else if( ch == 0 )
	{	
		for( ch = 1; ch <= 8; ch++)	
			digitalWrite( driverPin[ch], HIGH);
		driverOnOff = 0xff;
    }
}

void miniBCS::driverOff(uint8_t ch)
{
	if( (ch >= 1) && (ch <= 8) )
	{
		digitalWrite( driverPin[ch], LOW);
		driverOnOff &= ~(1 << (ch-1));
    }		
	else if( ch == 0 )
	{	
		for( ch = 1; ch <= 8; ch++)
			digitalWrite( driverPin[ch], LOW);
		driverOnOff = 0x00;
	}	
}

int8_t miniBCS::getDriver(uint8_t ch)
{
	if((ch >= 1) && (ch <= 8) )
		return driverOnOff & (1 << (ch-1));
	else if( ch == 0 )
		return driverOnOff;
	else	
		return -1;
		
}

void miniBCS::toneReset(void)
{  
	SPI.beginTransaction(DDS_SPI);
	SPI.transfer(0xff);    // dead transfer to get clock rest level set right	
	digitalWrite( DDSCSpin, LOW);	
	SPI.transfer16(0x0100);     // write control reg HOB
//	SPI.transfer(freqMode & 0x00ff);     // write control reg LOB
	digitalWrite( DDSCSpin, HIGH);	
	SPI.endTransaction();
	SOUND_ON_OFF = 1; //D6 = 1 to be off
}

void miniBCS::setToneGain(uint8_t level)
{  
	SPI.beginTransaction(POT_SPI);
	digitalWrite(POTCSpin, LOW);   // select pot    			
	SPI.transfer(0xc0 | 0);        // wiper write - ch 0
	SPI.transfer(level);
	digitalWrite(POTCSpin, HIGH);
	SPI.endTransaction();		
}
/*
void miniBCS::setDACGain(uint8_t level)
{  		   			
	SPI.beginTransaction(POT_SPI);
	digitalWrite(POTCSpin, LOW);   // select pot 
	SPI.transfer(0xc0 | 1);        // wiper write - ch 0
	SPI.transfer(level);
	digitalWrite(POTCSpin, HIGH);
	SPI.endTransaction();	
}
*/
void miniBCS::toneOff(void)
{
	SPI.beginTransaction(DDS_SPI);
	SPI.transfer(0xff);    // dead transfer to get clock rest level set right
	digitalWrite( DDSCSpin, LOW);	
	SPI.transfer16(0x20c0);           // use reset to turn off
	digitalWrite( DDSCSpin, HIGH);	
	SPI.endTransaction();
	SOUND_ON_OFF = 1; //D6 = 1 to be off
}

void miniBCS::toneOn(void)
{
	freqMode &= 0xfe3f;   // turn off sleep bits and reset
	SPI.beginTransaction(DDS_SPI);
	SPI.transfer(0xff);    // dead transfer to get clock rest level set right	
	digitalWrite( DDSCSpin, LOW);	
	SPI.transfer16(freqMode);     // write control reg HOB
//	SPI.transfer(freqMode & 0x00ff);     // write control reg LOB
	digitalWrite( DDSCSpin, HIGH);	
	SPI.endTransaction();
	SOUND_ON_OFF = 0; //D6 = 0 to be on
}

int8_t miniBCS::setTone( float freq, uint16_t mode) 
{
 uint16_t freqword;
 
    freqMode = mode;
	freqMode |= DDS_CONTROL; // form complete control register value 
	if ( SOUND_ON_OFF == 1) //sound is off, keep off
		freqMode |= 0x00c0;  // turn on sleep
	else
		freqMode &= 0xff3f;   // turn off sleep bits			
	ifreq = uint32_t (10.737418 * freq );   // 10.737418  = 2^28/25e  
	SPI.beginTransaction(DDS_SPI);
	SPI.transfer(0xff);    // dead transfer to get clock rest level set right	
	digitalWrite( DDSCSpin, LOW);	
	SPI.transfer16(freqMode); // >> 8);     // write control reg HOB
	//SPI.transfer(freqMode & 0x00ff);     // write control reg LOB
	freqword = 0x4000 | (ifreq & 0x3fff); // 14 LSBs 
	fwordl = freqword;
	SPI.transfer16( freqword); // >> 8 );
	//SPI.transfer( freqword & 0x00ff );
	freqword = 0x4000 | (ifreq >> 14) ;   // 14 MSBs	
	fwordh  = freqword;
	SPI.transfer16( freqword); // >> 8 );
	//SPI.transfer( freqword & 0x00ff );		
	digitalWrite( DDSCSpin, HIGH);	
	SPI.endTransaction();
    return 0;
	
}

uint16_t miniBCS::getToneMode(void)
{
	return freqMode;
}

int32_t miniBCS::getPosition(void)
{
	return _position;
}


void miniBCS::setPosition(int32_t newpos)
{
	_position = newpos;
}

  
  
  
  
  
  
  
  
  
  
  
  
  
  
  
  
  

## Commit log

2024-05-08 Board Update 20240508
    Add qwiic and SPI external connections
    [miniBCS-4_J005904.xlsx, miniBCS-4_J005904M.brd, miniBCS-4_J005904M.sch]
2024-05-21 Add SPI and I2C connectors
    Add external connections for SPI with two chip selects on 10 pin ribbon or 7 pin header
    Add QWIIC I2C connection
    [J005904_miniBCS-4.brd, J005904_miniBCS-4.dxf]
2024-07-17 Updated BOM, PCB files, example, and laser cut file
    Add QWIIC and SPI connector cutouts to laser file
    [miniBCS-4_J005904.xlsx, miniBCS-4_J005904M.brd, miniBCS-4_J005904M.dxf, miniBCS-4_J005904M.sch]
2025-01-11 Update BOM. example code
    [miniBCS-4_J005904.xlsx, untitled.dxf]
2025-07-28 Update example and PCB
    [J005904_miniBCS-4.brd, J005904_miniBCS-4.dxf]

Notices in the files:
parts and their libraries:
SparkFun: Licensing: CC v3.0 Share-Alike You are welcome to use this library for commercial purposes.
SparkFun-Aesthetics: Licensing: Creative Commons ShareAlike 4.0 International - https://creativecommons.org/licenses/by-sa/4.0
